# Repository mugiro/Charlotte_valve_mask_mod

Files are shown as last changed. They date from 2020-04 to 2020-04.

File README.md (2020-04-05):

# Acople de máscara de emergencia para ventiladores

La máscara de snorkel de superficie Easybreath fue propuesta por [isinnova.it](https://www.isinnova.it/easy-covid19-eng/) para hacer frente a la posible escasez de mascarillas hospitalarias. El inventor Dr. Favero desarrolló un nuevo componente para la conexión con el respirador, que se denominó válvula Charlotte. En este repositorio se encuentran las modificaciones, que partiendo de la pieza original, se han realizado con el fin de mejorar su fabricación y funcionalidad. Ni la máscara ni la conexión de la válvula tienen la certificación necesaria y su uso está supeditado a una situación de necesidad urgente. Las modificaciones y trabajos que a continuación se documentan no están ligadas a ninguna institución, entidad o actividad económica y son trabajos que se enmarcan enteramente dentro de las activiadades de investigación y desarrollo ejercidas por las personas que se encuentran reflejadas en el documento. Esta información ha sido compartida para mejorar la divulgación de los distintos estudios realizados y la busqueda de pontenciales aplicaciones en el futuro.

Se han desarrollado dos variantes del modelo original. La primera es una variante (Charlotte) que principalmente mejora el acoplamiento, pero intercambia las entradas y salidas, mientras que la segunda versión (llamada Isabel en honor a la doctora Isabel Muñoz) consigue mejores y más balanceados flujos de entrada de aire y elimina algunos de los problemas de fabricación en impresoras 3D. Ambas variantes mantienen el mismo sistema de anclaje y sellado con la mascara del Decathlon, pero el modelode 

Los cambios realizados han sido pensados para el uso del dispositivo en determinados tipos de pacientes. Para información sobre las ideas originales y potenciales usos del sistema dirigirse a [@Juan Luis Nicolás Barbajero](https://www.facebook.com/SEDATIO). Para información sobre los sistemas de fabricación y diseño de la adapcación tecnológica dirigirse a [@Andrés Sanz García](https://github.com/mugiro). Ganaremos y con vuestra ayuda, antes y mejor.

## Diferencias con los esquemas de montaje originales

El esquema inicial descargado de la pagina de [Isinnova](https://www.3dprintingmedia.network/forums/topic/charlotte-valve-by-isinnova-for-non-invasive-ventilator/) utilizaba las vías laterales de la mascara como elementos de salida y la vía central como elemento de entrada, tal y como se muestra en la siguiente figura:

<p align="center">
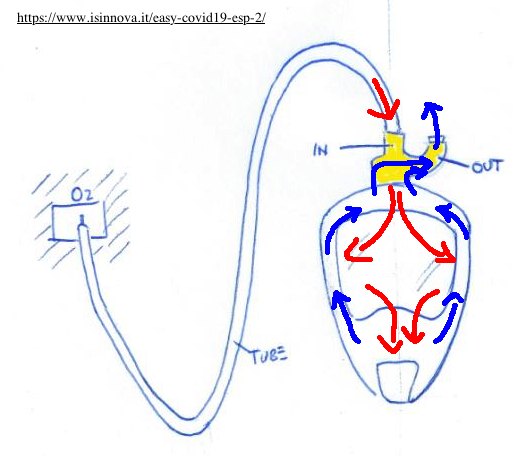
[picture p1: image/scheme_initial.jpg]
    
</p>

Sin embargo, y como se menciona en el punto anterior, el esquema actual intercambia dichos canales para ganar área de entrada. El nuevo esquema de circulación de flujo es el siguiente:

<p align="center">
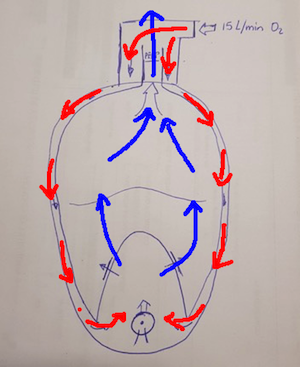
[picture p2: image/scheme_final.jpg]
    
</p>

## Modelo propuesto 1. Válvula de Charlotte modificada

<p align="center">
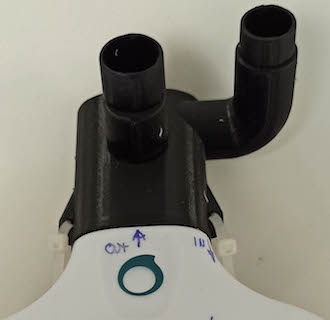
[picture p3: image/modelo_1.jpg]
    
</p>

Los principales cambios son los siguientes:
* **Estanqueidad**: Mejora de las estanqueidades por rediseño de la conexión, mayor ajuste con la goma tórica. Se insertan dos orejas que pueden ser utilizadas para apretar la conexión contra la junta tórica.
* **Orden conexiones**: Cambio de las conexiones de entrada y salida para facilitar la entrada de oxigeno en la parte inferior y reducir el volumen de la mascara.
* **Área de entrada**: La línea de la válvula PEEP (salida) será de un área total de 214 mm2.
* **Área de salida**: La línea de entrada del flujo oxígeno será la entrada curva con un área total de 424 mm2.
* **Valvulas interiores**: Importante!!! Cambio de posición de todas las válvulas de la máscara de buceo!!! Esto se realiza para permitir la salida del CO2 exhalado hacia la zona superior (de los ojos) y realizar una evacuación por la parte superior de la frente (canal central de la válvula).
* **Resistencia**: Rediseño y refuerzos de la estructura de la válvula mediante mayores grosores de pared.
* **Geometría**: Rediseño de curvas internas para mejorar el ajuste y la calidad de la impresión 3D de la pieza.
* **Cierre interior**: Se añade adhesivo en paredes interiores de la geometría cuadrada interior, para mejorar estanqueidad y mayor rigidez.
* **Sistema de agarre**: Eliminación de la pestaña de agarre y sustitución por un anclaje con bridas en los laterales de la valvula Charlotte.

## Modelo propuesto 2. Nuevo modelo con entrada balanceada de aire

<p align="center">
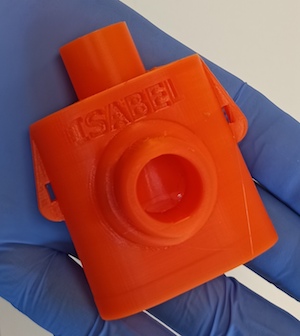
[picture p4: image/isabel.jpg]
    
</p>

Aparte de las mejoras logradas en la primera modificación, las principales nuevas mejoras de la valvula Isabel son las siguientes:

* **Estanqueidad**: Mejoras en el sellado del tubo de salida interior. 
* **Flujos de aire en el canal de entrada**: El canal de entrada permite introducir el flujo de aire de forma balanceada entre las dos zonas de la máscara y elimina los puntos de resistencia cinematica al aire. 
* **Tiempo de fabricación**: Tiempos de fabricación más cortos.

## Archivos STEP y STL

### Modelo propuesto 1: valvula Charlotte modificada
* [Descarga STEP v.3](step/charlotte_valve_v3.stp)
* [Descarga STL v.3](stl/charlotte_valve_v3.stl)

### Modelo propuesto 2: nueva versión Isabel  
* [Descarga STEP v.4](step/charlotte_isabel_v4.stp)
* [Descarga STL v.4](stl/charlotte_isabel_v4.stl)

## Instrucciones de montaje

En primer lugar se recomienda utilizar algun tipo de sellado en la parte interior en la sección cuadrada para mejorar la estanqueidad del sistema y evitar el intercambio de flujos entre entradas y saludas, justo en la junta de encuentro.

<p align="center">
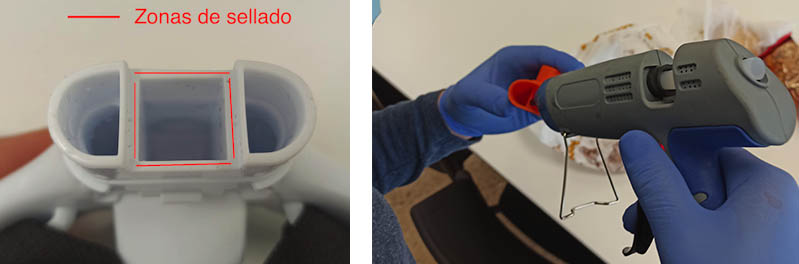
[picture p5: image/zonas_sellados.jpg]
    
</p>

La conexión del tubo con la mascara se ha ajustado para encajar en frío por presión simple ejercida siguiendo las instrucciones contenidas en el siguiente video:

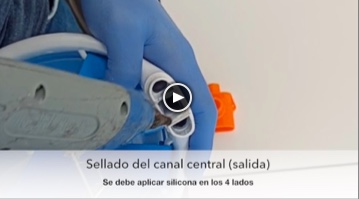
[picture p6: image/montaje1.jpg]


Esta operación hace que el conector de PLA presione la junta tórica y reduce drásticamente las posibles fugas en la unión. Es muy importante que el sistema encaje sin holguras y hemos detectados bastantes variaciones dimencionales entre las mascaras de un mismo modelo. En el caso de que el conector se quede atascado a la altura de la junta tórica, debemos presionar sobre ella manualmente con un destornilador fino o herramienta similar, para que el conector no pinze la junta tórica. 

Un cambio sobre el modelo inicial es la eliminación de las pestaña superiores que anclaba el conector Charlotte durante el montaje. Aunque más sencillo que nuestra propuesta, creemos que hemos conseguido un sistema más robusto, donde el número de roturas es practicamente cero si la pieza está correctamente impresa. Así pues, y para evitar que la conexión pierda estanqueidad el tiempo que está siendo utilizado el dispositivo por el paciente, se ha recurrido a un sistema de anclaje con bridas que mantiene la tensión siempre sobre la junta tórica y evita movimientos laterales que incrementen la holgura por deformación del PLA. Se han utilizado bridas de 150 x 2.5 mm de poliamida/nylon.

<p align="center">
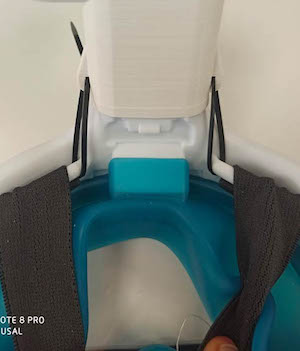
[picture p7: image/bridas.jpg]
    
</p>

Finalmente, y siguiendo el esquema inicial propuesto, se ha de girar todas y cada una de las válvulas de la máscara. Se incluyen fotos con la con las posiciones finales de las mismas a continuación:

<p align="center">
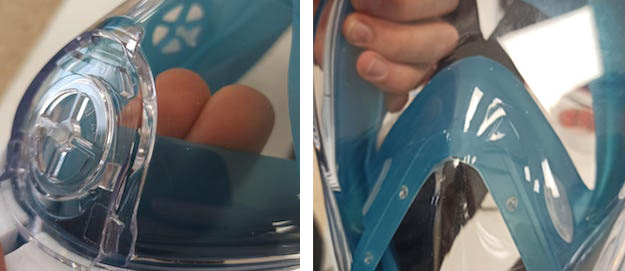
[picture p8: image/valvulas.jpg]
    
</p>

Una vez se finaliza su uso, para remover la valvula de la mascara, basta con cortar las bridas y aplicar calor sobre la válvula. El PLA pierde rigidez y se deforma facilmente a partir de los 60ºC, permitiendo su fácil extracción.
Es importante remarcar que el componente impreso es de un solo uso y ha de ser descartado como residuo biológico infeccioso. 

## Videos de las pruebas de montaje realizadas

A continuación se muestran los videos de las pruebas de montaje realizadas.
* **Montaje inicial con STL de origen**: [Link](https://www.facebook.com/SEDATIO/videos/2777854718995304 "Link");  [Descarga](video/test_initial.mp4)

* **Montaje final con STL modificado**:[Link](https://www.facebook.com/SEDATIO/videos/2785598748220901 "Link");  [Descarga](video/test_final.mp4)

* **Explicación montaje de valvula Charlotte modificada**:

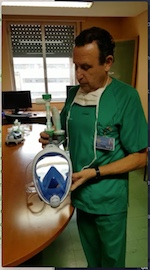
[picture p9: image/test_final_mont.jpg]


## Prototipado mediante impresión 3D

* **3D Printer**: Prusa MK3s

### Parámetros de impresión

* **Filament**: PLA filament 1.75 mm
* **Nozzle temperature**: 215 – 217 ° C
* **Builtplate temperature**: 60 ° C
* **Layer thickness**: 0.2 mm
* **Add. notes**: The supports are only touching the builtplate.
<p align="center">
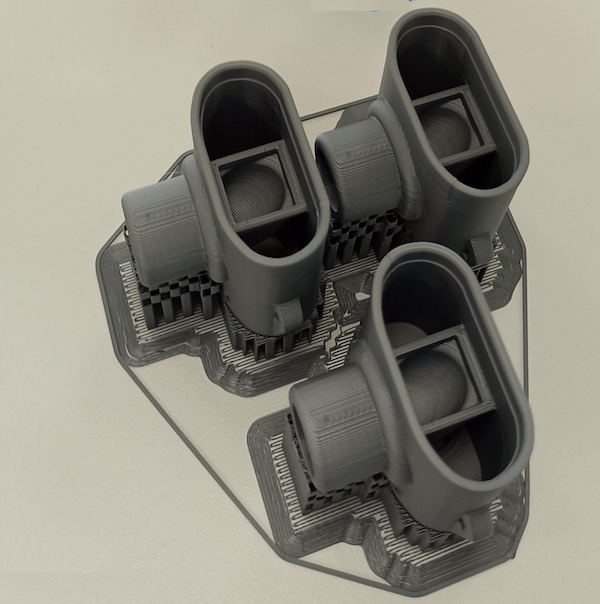
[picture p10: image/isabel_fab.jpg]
    
</p>

## Contactos

* **Armando González Muñoz** - Spain - [@armandopeska](https://github.com/armandopeska)
* **Juan Luis Nicolás Barbajero** - Spain - [@JuanLuis](https://www.facebook.com/SEDATIO)
* **Andres Sanz Garcia** - Spain - [@mugiro](https://github.com/mugiro)

## Other information

Print impressions of the Charlotte valve By Jan Sebastian van Ackeren and Jerry de Vos. [Ackeren](https://docs.google.com/document/d/1nmjyFOHmBbaKG4P3CZGqO-naOPvYvfRFZUZONSgWS88/edit)

File Source: Charlotte Valve by Isinnova for non-invasive [Isinnova](https://www.3dprintingmedia.network/forums/topic/charlotte-valve-by-isinnova-for-non-invasive-ventilator/)

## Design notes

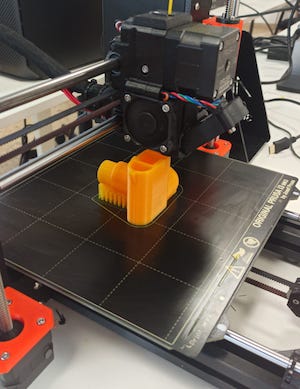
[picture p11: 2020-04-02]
image/prusa.jpg

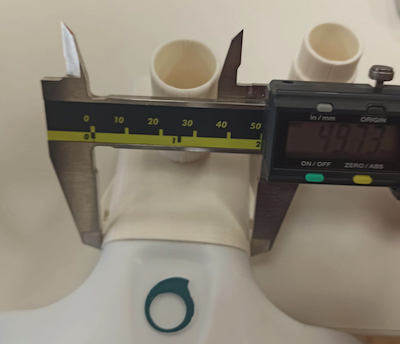
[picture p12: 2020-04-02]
image/ajuste_final.jpg

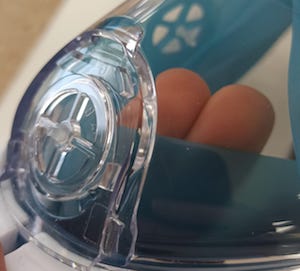
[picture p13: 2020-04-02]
image/valvula_frontal.jpg

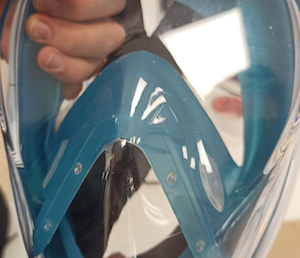
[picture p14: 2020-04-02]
image/valvulas_interiores.jpg

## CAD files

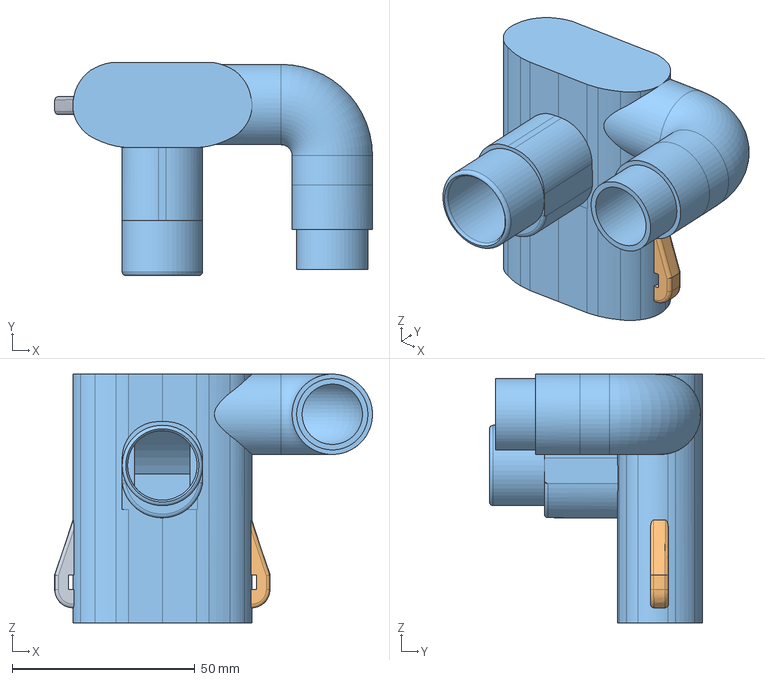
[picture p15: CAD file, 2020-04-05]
step/charlotte_valve_v3.stp
87.0 x 58.3 x 68.1 mm

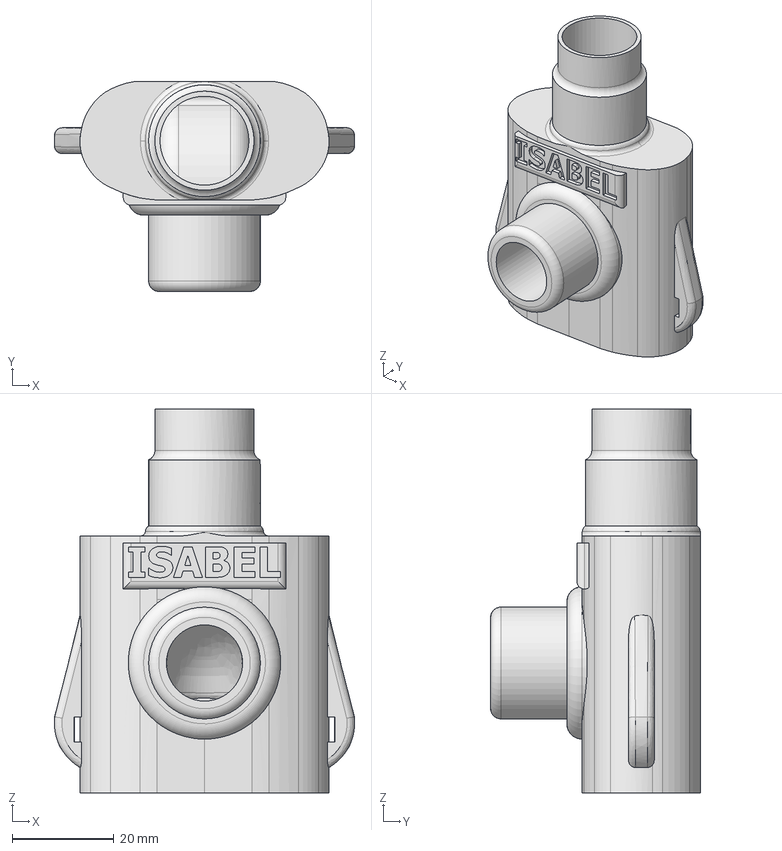
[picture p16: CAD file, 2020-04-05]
step/charlotte_isabel_v4.stp
59.1 x 41.3 x 75.6 mm

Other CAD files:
stl/charlotte_isabel_v4.stl
stl/charlotte_valve_v3.stl

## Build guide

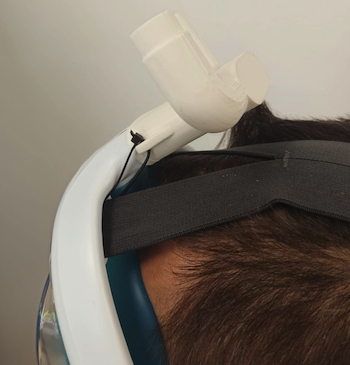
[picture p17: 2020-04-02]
image/montaje_final_2.jpg

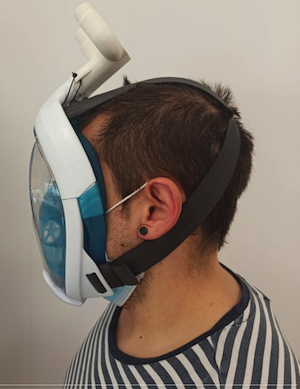
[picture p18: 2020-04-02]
image/montaje_final_1.jpg
